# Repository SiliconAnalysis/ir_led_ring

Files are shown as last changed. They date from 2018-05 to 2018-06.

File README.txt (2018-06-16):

IR LED ring (ILR) illuminator
Designed to be used with Mitutoyo M Plan IR objectives

Design summary:
-ilr-ext: externally powered LED array, all in series
    ie use lab bunch supply
    r1
        scrapped due to error in inner diameter
    r2
        Shrunk ID
        Add IR warning
        Clean up mounting holes
    TODO: add fuse
    TODO: possibly increase LED hole to help set angle
-solder_jig
    Places LEDs at 45 degree angle for above assembly
-ilr-lm317: LM317 design with 12V in regulating to fixed 100 mA
    Does not work / don't use
-ilr-r: 12V in resistor limiting to around 100 mA
    Does not work / don't use

Max LED power
150 mW dissipation
100 mW current => 8 mW optical
1.4 Vdrop max => 1.4 * 0.1 = 140 - 8 mW = 132 mW
1.25 Vdrop typ => 1.25 * 0.1 = 125 - 8 mW = 117 mW
Safe to run at 100 mW continuously, assuming reasonable 25C air flow

Mityotyo M Plan APo objective measurements
Note: https://www.edmundoptics.com/microscopy/infinity-corrected-objectives/Mitutoyo-NIR-NUV-and-UV-Infinity-Corrected-Objectives/
Note: https://www.edmundoptics.com/microscopy/infinity-corrected-objectives/Mitutoyo-Infinity-Corrected-Long-Working-Distance-Objectives/
Main diameter: 32.25 mm
Objective to objective clearance on main area up to knurled area: ~30 mm
    Total clearance diameter: 32.25 + 30/2 = 47.25 mm
    Try to keep below 45
Knurled diameter: 34.00 mm
Flat area to knurled (10x objective): ~20.5 mm
Mityotyo sample working distances (note: multiple versions)
    Mag     WD
    5x      37.5
    10x     30.5
    20x     20,25.5
    50x     10,17
    100x    10,12

Dimension proposals
LEDs at 50 mm diameter
LEDs are 8.6 mm high => 10 mm approximately with standoff
Middle of PCB cut to 33 mm (touch up with file if necessary)

45 degree angle seems good starting point
What would focal point be at?
distance = 25 * sin(45) = 17.7 mm
limits use to the 20x objective

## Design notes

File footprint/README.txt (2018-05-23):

https://raw.githubusercontent.com/Kazu-zamasu/KiCAD-foot-print/master/Hobby-Devices.pretty/DCJack(EJ508A-ND).kicad_mod
https://github.com/Kazu-zamasu/KiCAD-foot-print

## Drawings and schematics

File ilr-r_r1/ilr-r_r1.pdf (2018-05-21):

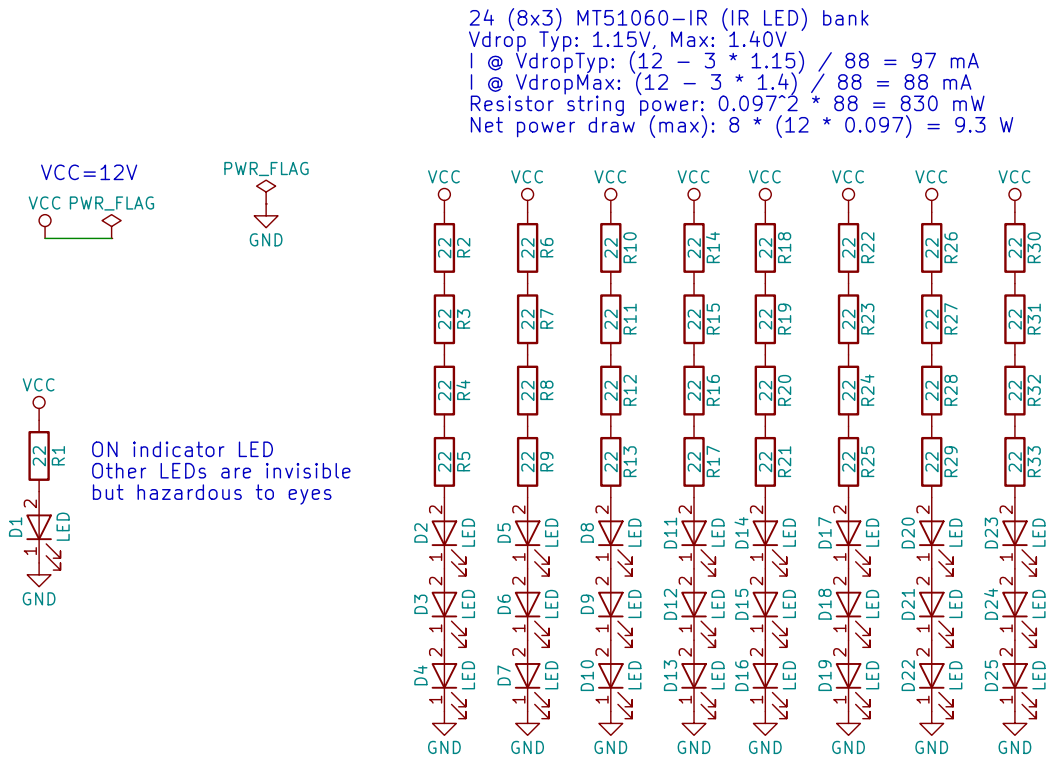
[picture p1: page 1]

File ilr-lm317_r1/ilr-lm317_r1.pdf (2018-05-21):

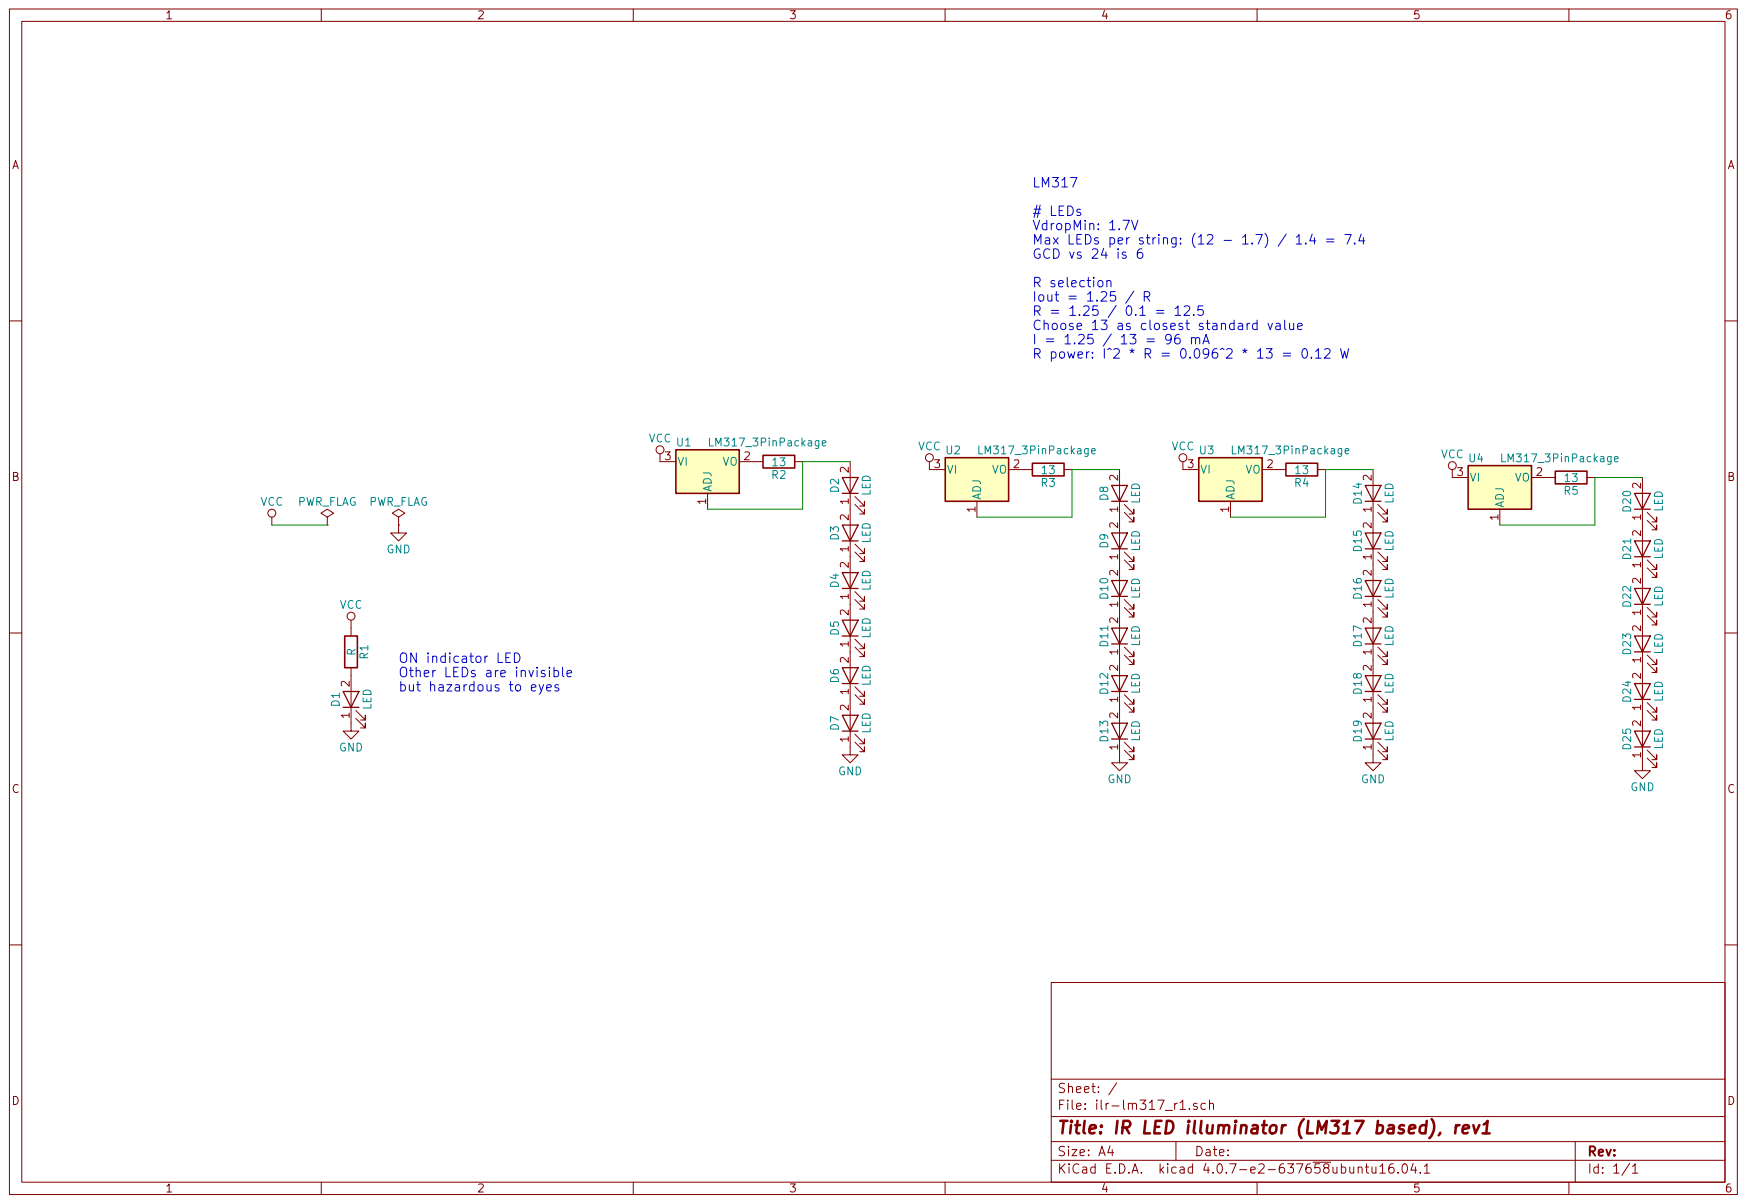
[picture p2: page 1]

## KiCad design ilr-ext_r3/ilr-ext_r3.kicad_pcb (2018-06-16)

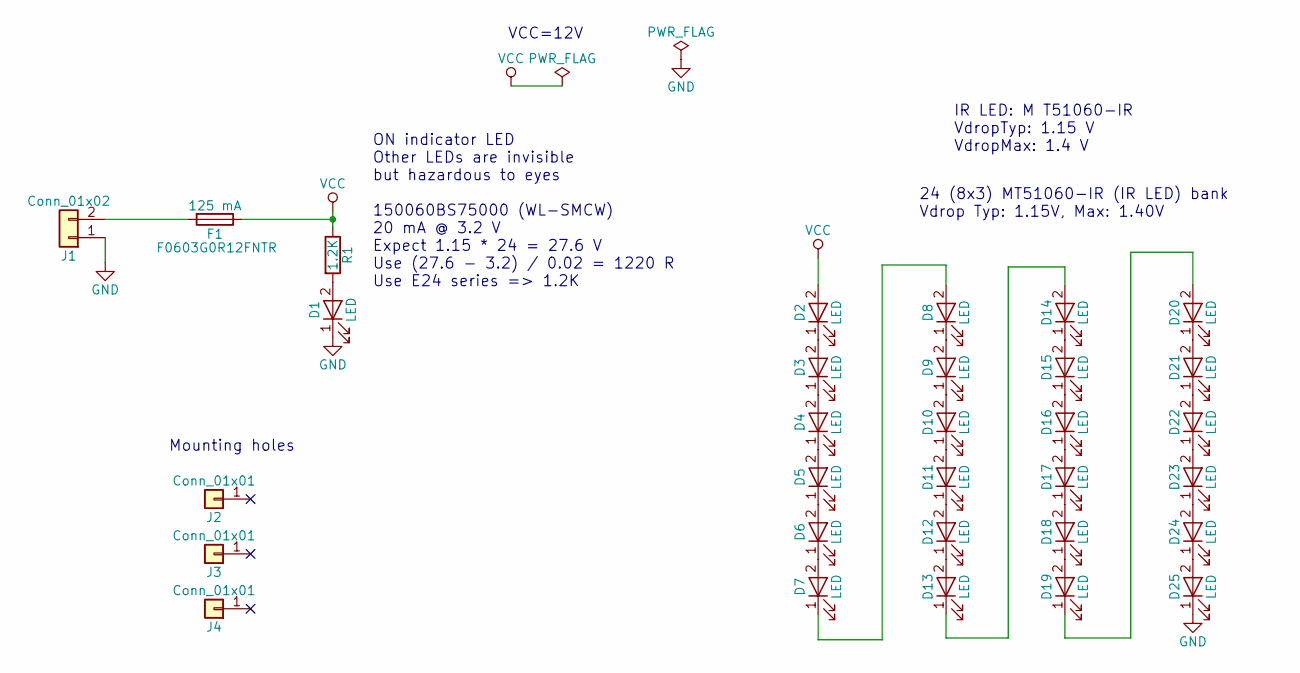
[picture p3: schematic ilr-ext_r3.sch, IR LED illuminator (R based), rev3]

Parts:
D1: LED; LED_0603
D2, D3, D4, D5, D6, D7, D8, D9, D10, D11, D12, D13, D14, D15, D16, D17, D18, D19, D20, D21, D22, D23, D24, D25: LED; LED_D5.0mm
F1: 125 mA; R_0603
J1: Conn_01x02; Pin_Header_Straight_1x02_Pitch2.54mm
J2, J3, J4: Conn_01x01; MountingHole_3.5mm
R1: 1.2K; R_0603

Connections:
GND: D1.1 (K), D25.1 (K), J1.1
unnamed: D1.2 (A), R1.2
unnamed: D2.1 (K), D3.2 (A)
unnamed: D3.1 (K), D4.2 (A)
unnamed: D4.1 (K), D5.2 (A)
unnamed: D5.1 (K), D6.2 (A)
unnamed: D6.1 (K), D7.2 (A)
unnamed: D7.1 (K), D8.2 (A)
unnamed: D8.1 (K), D9.2 (A)
unnamed: D10.1 (K), D11.2 (A)
unnamed: D9.1 (K), D10.2 (A)
unnamed: D11.1 (K), D12.2 (A)
unnamed: D12.1 (K), D13.2 (A)
unnamed: D13.1 (K), D14.2 (A)
unnamed: D14.1 (K), D15.2 (A)
unnamed: D15.1 (K), D16.2 (A)
unnamed: D16.1 (K), D17.2 (A)
unnamed: D17.1 (K), D18.2 (A)
unnamed: D18.1 (K), D19.2 (A)
unnamed: D19.1 (K), D20.2 (A)
unnamed: D20.1 (K), D21.2 (A)
unnamed: D21.1 (K), D22.2 (A)
unnamed: D22.1 (K), D23.2 (A)
unnamed: D23.1 (K), D24.2 (A)
unnamed: D24.1 (K), D25.2 (A)
unnamed: F1.2, J1.2
VCC: D2.2 (A), F1.1, R1.1

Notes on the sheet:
ON indicator LED Other LEDs are invisible but hazardous to eyes 150060BS75000 (WL-SMCW) 20 mA @ 3.2 V Expect 1.15 * 24 = 27.6 V Use (27.6 - 3.2) / 0.02 = 1220 R Use E24 series => 1.2K
24 (8x3) MT51060-IR (IR LED) bank Vdrop Typ: 1.15V, Max: 1.40V
VCC=12V
IR LED: M T51060-IR VdropTyp: 1.15 V VdropMax: 1.4 V
Mounting holes

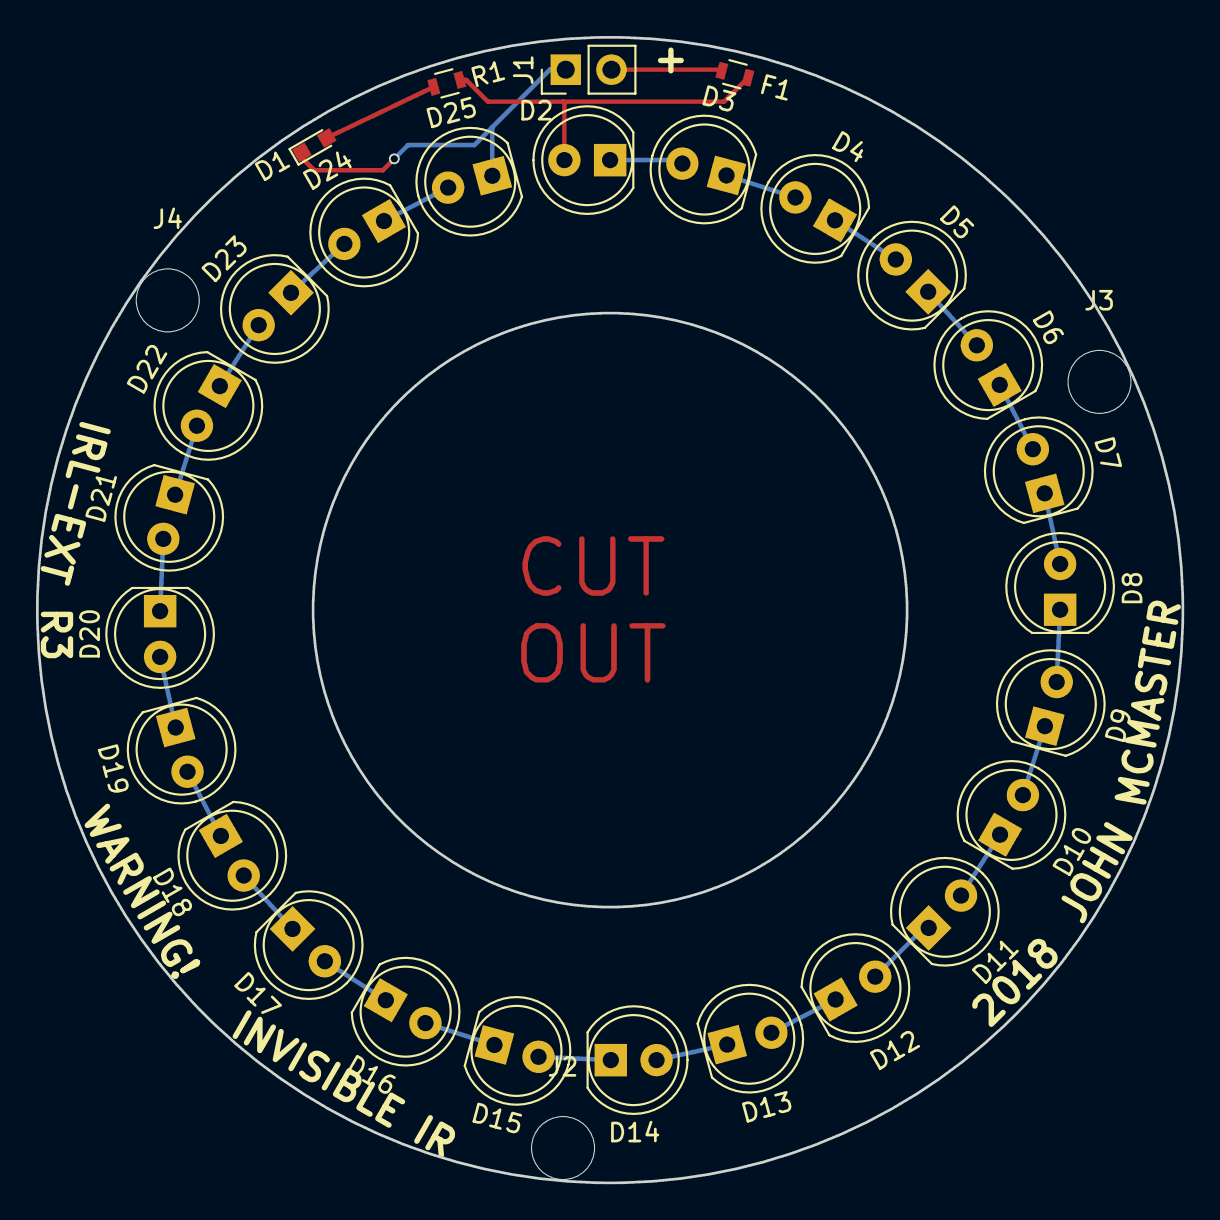
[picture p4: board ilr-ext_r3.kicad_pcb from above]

Board: 2 copper layers, 63.6 x 63.6 mm, 31 parts (0 on the bottom side), 27 nets.

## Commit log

2018-05-21 Illuminator schematic (LM317 based)
    [ilr-lm317_r1.kicad_pcb, ilr-lm317_r1.sch]
2018-05-21 Illuminator schematic (R based)
    [ilr-r_r1.sch]
2018-06-13 sync files
    [ilr-ext_r1.kicad_pcb, ilr-ext_r1.sch, ilr-r_r1.kicad_pcb]
2018-06-16 ilr-ext_r3: future build tweaks
    [ilr-ext_r2.kicad_pcb, ilr-ext_r2.sch, ilr-ext_r3.kicad_pcb, ilr-ext_r3.sch]
